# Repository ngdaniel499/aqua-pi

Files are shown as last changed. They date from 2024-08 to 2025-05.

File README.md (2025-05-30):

# AquaPi
Documentation for the Raspberry Pi based water quality monitoring system created by Daniel P. Harrison

## Pi first time setup
### Flash OS
#### Windows
Download Raspberry pi imager https://www.raspberrypi.com/software/

Raspberry Pi Device: Raspberry Pi 1

Operating System: Raspberry PI OS Lite (32-BIT)
	
 	PRETTY_NAME="Raspbian GNU/Linux 12 (bookworm)"
	NAME="Raspbian GNU/Linux"
	VERSION_ID="12"
	VERSION="12 (bookworm)"
	VERSION_CODENAME=bookworm
	ID=raspbian
	ID_LIKE=debian
	HOME_URL="http://www.raspbian.org/"
	SUPPORT_URL="http://www.raspbian.org/RaspbianForums"
	BUG_REPORT_URL="http://www.raspbian.org/RaspbianBugs"
	 
OS Customisation settings: 

	Services>Enable SSH, 

	General>Set username/pw, 

	General>Configure Wireless LAN: add SSID/pin, 

	General>Set Locale settings>Time Zone: Sydney, 

	General>Set Locale settings>Keyboard Layout: US

### RPi setup
  
	sudo apt-get update

	sudo apt-get upgrade

#### configure startup for 1-wire and wlan0
	sudo nano /etc/rc.local
	#!/bin/sh -e
 
	ip link set eth1 down

 	ip link set eth0 down
 
  	ip link set usb0 down
     
	sudo modprobe w1-gpio
	
	sudo modprobe w1-therm

	exit 0
 
#### Turn on 1-wire

Refernce: https://learn.adafruit.com/adafruits-raspberry-pi-lesson-11-ds18b20-temperature-sensing/ds18b20

	sudo raspi-config

		Interfacing Options > 1-Wire > Yes

	sudo reboot

#### Install aqua-pi files and dependencies and setup virtual environment
	sudo apt install git python3 python3-pip -y 
 
 	# if "failed to fetch error / internect connection isn't working delete other connections (nmcli con delete "Wired connection 2")
  
  	cd ~
  
 	git clone https://github.com/ngdaniel499/aqua-pi.git
 
	cd ~/aqua-pi

	python3 -m venv .venv

	source .venv/bin/activate

	pip install -r requirements.txt

#### Configure aquapi

 	cd python-scripts

  	cp Upconfig_template.cfg Upconfig.cfg

 	#edit station name, pump (if required), calibration if data is available. update server IP
  
   	nano Upconfig.cfg 

 	# install cronjob
  
	crontab cronjob.txt

	# edit config if necessary
  
	crontab -e

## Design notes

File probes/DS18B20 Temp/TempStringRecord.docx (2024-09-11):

SIMS SHRP – Sydney Harbour Real Time Monitoring

Daniel Harrison

Dallas DS18B20 Submersible temperature strings record

String ID | Sensor ID (from top) | Position | Nominal Depth | Serial | Cal Correct
001 | 1 | 1m up | | 00000474c314
001 | 2 | Bottom | | 000004756430

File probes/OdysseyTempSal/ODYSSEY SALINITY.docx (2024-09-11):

ODYSSEY SALINITY / TEMP DATA LOGGER

Note that this only covers the trace mode as I have a lot more workto do on other modes of operation.

Trace Mode:

Baud Rate 4800

Parity None

Data Bits 8

Stop Bits 1

Input Buffer Size 32000

1. Software

To wake up the logger send a train of pulses i.e 0x01 01 01 01 01 01 01.

2. Logger

When the logger detects the above pulses it responds with the ascii string

'Hi!' (0x48, 69, 21).

3. Software

The software then confirms logger response and sends String 'T' (0x54)

followed by the ID number of the logger. For the conductivity logger the ID

is 0x1A (Decimal 26).

The software then needs to go into a state waiting for the logger to send

serial data.

4. Logger

Sends values to the software in what appears to be a constant data stream.

The software counts in each byte which is processed and displayed (see raw

data processing below).

If the logger reaches 64 readings it's sends a stop command to the software

(stop command TBD).

Raw Data Processing:

The logger sends data to the software representing the environment it is

monitoring.

This data is processed in such a way as to make the maximum value capable of

being recorded = 65535

Example:

Logger sends 0x09 13.

Binary conversion = 00001001 00010011

Decimal Conversion: MSB = 9 LSB = 19

Software Conversion = MSB + (LSBx256)

i.e. 9 + (19 x 256) = (9 + 4864) = 4873

To exit the trace mode repeat steps 1 & 2 above. The logger will again

respond with the ascii string 'Hi!' (0x48, 69, 21) to confirm it has

stopped.

Hi Daniel,

Yes, we can retrieve the calibration figures if we have the serial numbers.

Engineer

You can get the software to download the data from our website:

http://odysseydatarecording.com/index.php?route=product/category&path=66

The manual is also available:

http://odysseydatarecording.com/index.php?route=information/information&information_id=9

You will also need the calibration files for the units, did they come with

the loggers?

Regards

Richard

Engineer

With reference to the photo supplied:

Green/White = Ground

Blue /White = Transmit (Tx)

Black/White = Recieve (Rx)

Hi Daniel,

Great to hear you are still working on the SHED project. I'm still doing sensor related work but more on the server side infrastructure. Our marine related work (in aquaculture) has stepped up one cost level and we now use embedded Linux and various high cost sensors like Tyco EC250 etc.

Your experience with Odyssey sensors matches exactly with ours. Their tech support is less than helpful. You are right we did reverse engineer the sensor communication. I believe we basically replay communication we captured from the windows software. I do remember thinking is was a bit odd.

Below is a code snippet that may help. This is basically replicating what we saw in our data capture. You should be able to port that across to what ever platform you are using. The last part about sending 256 0x01 bytes is what we saw in the capture. We were never quite sure why it was there! maybe some kind of reset mechanism.

Anyway, hopefully that helps.

Cheers

Chris

//write 0x01 to serial

odyssey_buf[0]=0x01;

i = fos_serial_write(odyssey_serial, odyssey_buf, 1);

if (i != 1) goto fail;

// Brief pause of 0.8 second...

fos_vartimer_sleep(800);

//write 0x54, 0x1a to serial...

odyssey_buf[0]=0x54;

i = fos_serial_write(odyssey_serial, odyssey_buf, 1);

if (i != 1) goto fail;

odyssey_buf[0]=0x1a;

i = fos_serial_write(odyssey_serial, odyssey_buf, 1);

if (i != 1) goto fail;

//next read 4 serial bytes or timeout...

//first erase the odyssey_buffer, flush the serial port ...

for(i=0;i<4;i++)

odyssey_buf[i]=0;

fos_serial_flush (odyssey_serial);

if(fos_serial_timed_read(odyssey_serial,odyssey_buf,4,4)==4)

{

*temperature = (uint16_t)(odyssey_buf[0]) | (((uint16_t)(odyssey_buf[1]))<<8);

*conductivity = (uint16_t)(odyssey_buf[2]) | (((uint16_t)(odyssey_buf[3]))<<8);

success = FOS_TRUE;

} else {

success = FOS_FALSE;

}

//write 0x01 to serial about 256 times...

for(i=0;i<4;i++)

odyssey_buf[i]=0x01;

for(i=0;i<64;i++)

{

fos_serial_write(odyssey_serial, odyssey_buf, 4);

}

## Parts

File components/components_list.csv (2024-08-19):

Item | Description | Cost | Link | Notes
10A PWM Solar Charge Controller 12/24V with USB | - Automatic charge mode selection - Suitable for 12V and 24V battery banks - USB charging port on front panel - Charging Modes: Bulk, Equalise, Float - Supports: Sealed, Gel and Flooded - USB Output: 5V @ 1.2A - Terminals to suit cable up to 4mm2. | $56.95 | https://www.jaycar.com.au/10a-pwm-solar-charge-controller-1224v-with-usb/p/MP3750 | Optional for first experiment
12V 5W Solar Panel with Lead/Clips | 251x205x18mm 5W max power 0.67kg 3m cable | $24.95 | https://www.jaycar.com.au/12v-5w-solar-panel-with-leadclips/p/ZM9050 | Optional for first experiment, could be good to experiment with solar power. Probably need larger solar panel for multiple biopods
Giantz AGM Deep Cycle Battery 12V 25Ah Box Portable Solar Caravan Camping | Overall dimensions: 18 x 7.6 x 16.5 cm Approx. weight: 5.8KG Maximum cycle lIfe: 1400 cycles (@30% DOD) | $ 65 95 | https://www.bigw.com.au/product/giantz-agm-deep-cycle-battery-12v-25ah-box-portable-solar-caravan-camping/p/9900022130 | Should be good enough for first experiment (without solar charging). Might need upgrading for multiple biopods
Linux supported wifi adapter | Wi-Fi 4 802.11n Adapter for PC N150 Nano USB Adapter, 150Mbps, Smallest Wi-Fi 4 Dongle, Win 11 Plug-n-Play, Linux: Ubuntu/Mint Plug-n-Play for Kernel 5.15 and Above, Mac OS, EW-7811Un V2 | 18.09 | https://www.amazon.com/gp/product/B08F2ZNC6J?camp=1789&creative=9325&creativeASIN=B08F2ZNC6J&linkId=80939d577c76fb60d3eb468c10f5b1ba | Driver support for generic wifi adapters might be limited. This one seems to work with Rpi
Telstra Prepaid 4GX Hotspot Black MF985T | It supports speeds up to 600 Mbps. It can support up to 20 devices connected at a time. It has 2 external antenna Ports (antennas not included) for broader coverage. It uses the Telstra 4G network for swift internet access. A 12 month warranty is included. | $149.00 | https://www.officeworks.com.au/shop/officeworks/p/telstra-prepaid-4gx-hotspot-black-mf985t-te210076 | 4G coverage seems sufficient. 4G+5G would be most reliable https://www.telstra.com.au/coverage-networks/our-coverage. Matt might have a better suggestion if he's more familiar with networking
Variable power suppply | - Variable output voltage: 3V DC to 15VDC - Fixed voltage mode: 13.8V DC - Max. output current 40 Amps (continuous) - Ripple & noise: 10m Vrms - Load regulation: 230mV @ 0 - 100% load. - Measures 220(W) x 110(H) x 300(L)mm. - Incredibly light, weighing only 3.5Kgs. - Switchmode | 42.6 | https://www.jaycar.com.au/3v-to-15-volt-dc-40-amp-regulated-switchmode-laboratory-power-supply/p/MP3090 | For testing the system

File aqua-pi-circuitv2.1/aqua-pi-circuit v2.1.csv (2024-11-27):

Id | Designator | Footprint | Quantity | Designation | Supplier and ref
1 | relay control | PinSocket_1x05_P2.54mm_Horizontal | 1 | Conn_01x05_Pin
2 | R1,R4,R3 | R_Axial_DIN0204_L3.6mm_D1.6mm_P5.08mm_Horizontal | 3 | 1k
3 | R2 | R_Axial_DIN0204_L3.6mm_D1.6mm_P5.08mm_Horizontal | 1 | 2k
4 | Chla gain | PinSocket_1x02_P2.54mm_Horizontal | 1 | Conn_01x02_Pin
5 | Sensor in | PinSocket_1x08_P2.54mm_Horizontal | 1 | Conn_01x08_Pin
6 | C2 | C_Disc_D3.0mm_W1.6mm_P2.50mm | 1 | 1uF
7 | J5 | PinSocket_1x02_P2.54mm_Horizontal | 1 | Conn_01x02
8 | RPI | PinHeader_2x20_P2.54mm_Vertical | 1 | Conn_02x20_Odd_Even
9 | Q2,Q1 | TO-92_Inline | 2 | BC549
10 | U1 | PDIP16_300MC_MCH | 1 | MCP3208
11 | C1 | C_Disc_D3.0mm_W1.6mm_P2.50mm | 1 | 100nF

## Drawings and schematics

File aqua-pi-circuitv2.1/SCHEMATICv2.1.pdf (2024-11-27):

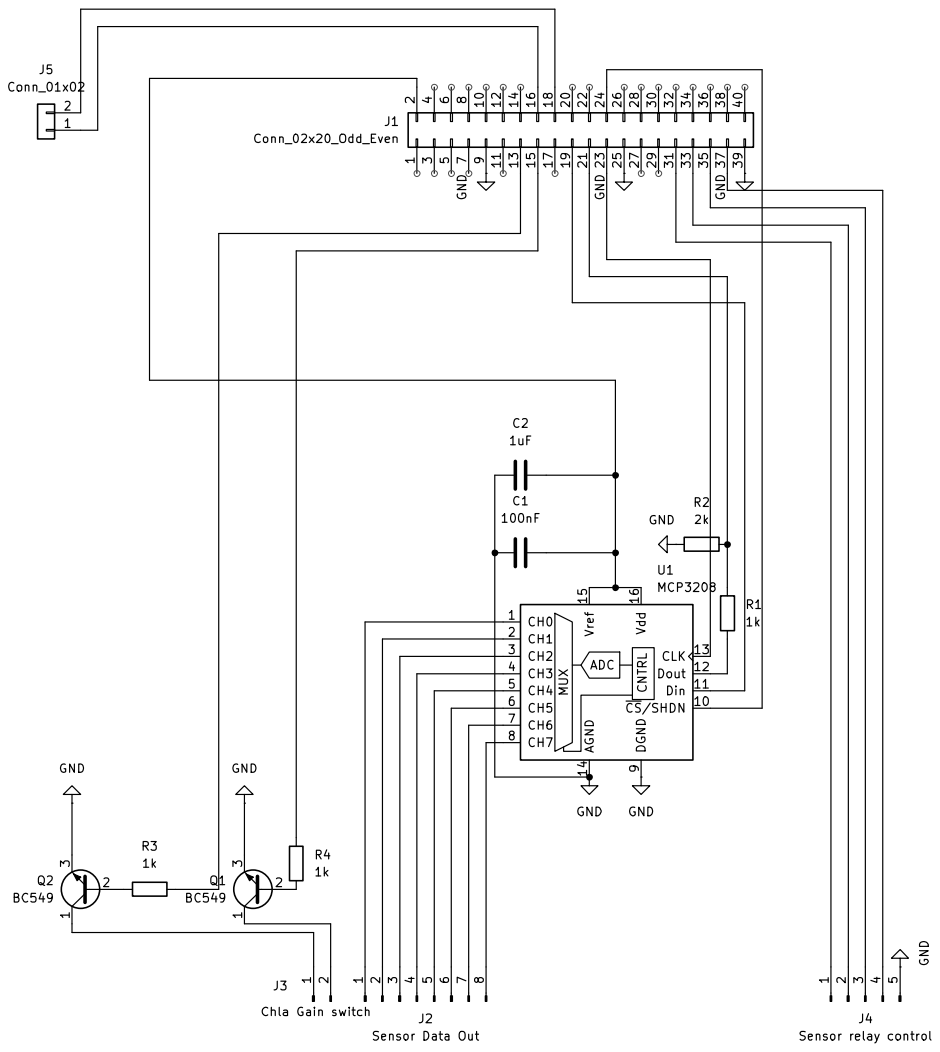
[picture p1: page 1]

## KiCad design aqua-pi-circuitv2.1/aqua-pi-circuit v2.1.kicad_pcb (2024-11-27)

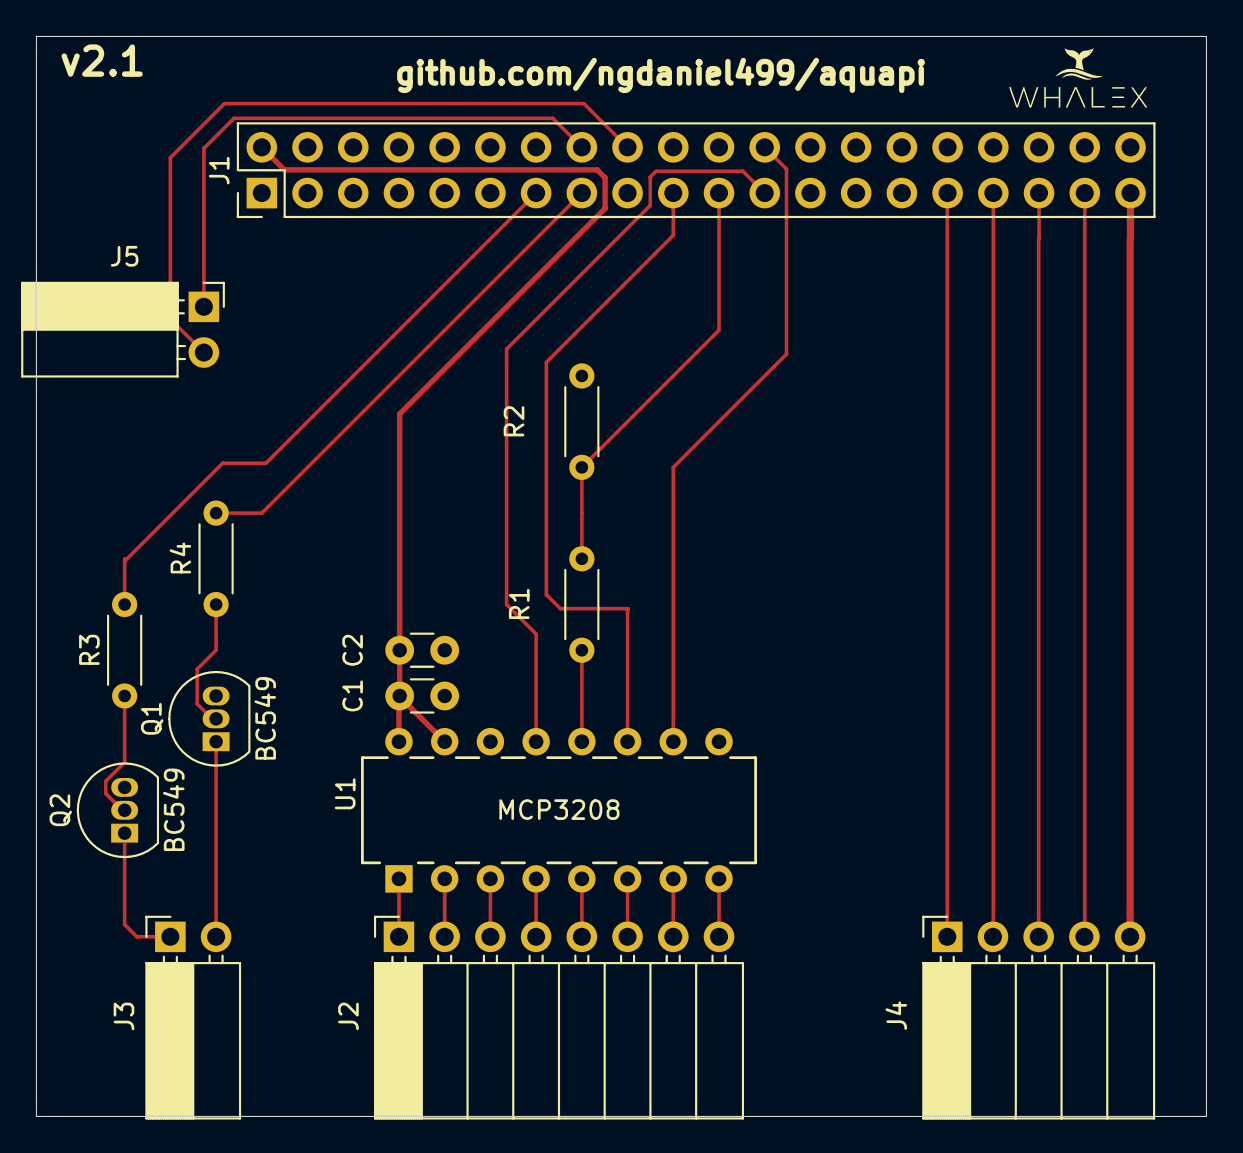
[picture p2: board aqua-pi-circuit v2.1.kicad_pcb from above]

Board: 2 copper layers, 65.0 x 60.0 mm, 14 parts (0 on the bottom side), 27 nets.

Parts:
C1: 100nF; C_Disc_D3.0mm_W1.6mm_P2.50mm
C2: 1uF; C_Disc_D3.0mm_W1.6mm_P2.50mm
J1: Conn_02x20_Odd_Even; PinHeader_2x20_P2.54mm_Vertical
J2: Conn_01x08_Pin; PinSocket_1x08_P2.54mm_Horizontal
J3: Conn_01x02_Pin; PinSocket_1x02_P2.54mm_Horizontal
J4: Conn_01x05_Pin; PinSocket_1x05_P2.54mm_Horizontal
J5: Conn_01x02; PinSocket_1x02_P2.54mm_Horizontal
Q1, Q2: BC549; TO-92_Inline
R1, R3, R4: 1k; R_Axial_DIN0204_L3.6mm_D1.6mm_P5.08mm_Horizontal
R2: 2k; R_Axial_DIN0204_L3.6mm_D1.6mm_P5.08mm_Horizontal
U1: MCP3208; PDIP16_300MC_MCH

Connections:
GND: C1.1, C2.1, J1.9, J1.25, J1.39, J4.5, Q1.3 (E), Q2.3 (E), R2.1, U1.9 (DGND), U1.14 (AGND)
unnamed: C1.2, C2.2, J1.2, U1.15 (Vref), U1.16 (Vdd)
unnamed: J1.13, R3.2
unnamed: J1.15, R4.2
unnamed: J1.16, J5.1
unnamed: J1.18, J5.2
unnamed: J1.19, U1.11 (Din)
unnamed: J1.21, R1.1, R2.2
unnamed: J1.23, U1.13 (CLK)
unnamed: J1.24, U1.10 (~CS/SHDN)
unnamed: J1.31, J4.1
unnamed: J1.33, J4.2
unnamed: J1.35, J4.3
unnamed: J1.37, J4.4
unnamed: J2.1, U1.1 (CH0)
unnamed: J2.2, U1.2 (CH1)
unnamed: J2.3, U1.3 (CH2)
unnamed: J2.4, U1.4 (CH3)
unnamed: J2.5, U1.5 (CH4)
unnamed: J2.6, U1.6 (CH5)
unnamed: J2.7, U1.7 (CH6)
unnamed: J2.8, U1.8 (CH7)
unnamed: J3.1, Q2.1 (C)
unnamed: J3.2, Q1.1 (C)
unnamed: Q1.2 (B), R4.1
unnamed: Q2.2 (B), R3.1
unnamed: R1.2, U1.12 (Dout)

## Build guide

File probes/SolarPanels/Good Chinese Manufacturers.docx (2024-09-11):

Chinese Manufacturers classed as ‘Tier 1 in Australia’ (in my humble opinion)

- Canadian Solar
- CNPV
- CSUN
- Daqo
- ET Solar
- JA Solar
- Jinko Solar
- LDK
- Renesola
- SunTech
- Trina Solar
- Yingli

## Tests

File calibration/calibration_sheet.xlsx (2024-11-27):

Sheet: Sheet1
Serial / material | Blank | AVERAGE RAW READING 400ppb RWT DYE(40ug/L chla equiv) | Calibration curve | Gain setting | Calibration liquid | date
2103415 Titanium | 0 | 838.9090909 | 0.04768097096 | 10x | 400ppb rhodamine WT dye | 2024-10-01
2180450 plastic | 0 | 2020.8 | 0.01979414093 | 10x | 400ppb rhodamine WT dye | 2024-10-01
2180556 plastic | 0 | 2662.5 | 0.01502347418 | 10x | 400ppb rhodamine WT dye | 2024-10-01

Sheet: 2180450
Time | Probe_TempRaw | Probe_TempCal | Condraw | CondCal | SpCond | Salinity | TurbRaw | TurbCal | TurbManu | ChlRaw | ChlVolts | ChlCal | CDOMRaw | CDOMVolts | CDOMCal | CDOMChlEQ | ChlAdj | TempRaw | TempCal
2024-10-17 | Fail | Fail | Fail | Fail | Fail | Fail | Fail | Fail | Fail | 1984 | 1.5984375 | 10.9112 | 0 | 0 | 0 | 0 | 10.9112 | 800 | 6.86
2024-10-17 | Fail | Fail | Fail | Fail | Fail | Fail | Fail | Fail | Fail | 1972 | 1.588769531 | 10.8428 | 0 | 0 | 0 | 0 | 10.8428 | 792 | 6.7752
2024-10-17 | Fail | Fail | Fail | Fail | Fail | Fail | Fail | Fail | Fail | 2064 | 1.662890625 | 11.3672 | 0 | 0 | 0 | 0 | 11.3672 | 793 | 6.7858
2024-10-17 | Fail | Fail | Fail | Fail | Fail | Fail | Fail | Fail | Fail | 2050 | 1.651611328 | 11.2874 | 0 | 0 | 0 | 0 | 11.2874 | 781 | 6.6586
2024-10-17 | Fail | Fail | Fail | Fail | Fail | Fail | Fail | Fail | Fail | 2010 | 1.619384766 | 11.0594 | 0 | 0 | 0 | 0 | 11.0594 | 790 | 6.754
2024-10-17 | Fail | Fail | Fail | Fail | Fail | Fail | Fail | Fail | Fail | 2035 | 1.639526367 | 11.2019 | 0 | 0 | 0 | 0 | 11.2019 | 797 | 6.8282
2024-10-17 | Fail | Fail | Fail | Fail | Fail | Fail | Fail | Fail | Fail | 1998 | 1.609716797 | 10.991 | 0 | 0 | 0 | 0 | 10.991 | 791 | 6.7646
2024-10-17 | Fail | Fail | Fail | Fail | Fail | Fail | Fail | Fail | Fail | 2018 | 1.625830078 | 11.105 | 0 | 0 | 0 | 0 | 11.105 | 783 | 6.6798
2024-10-17 | Fail | Fail | Fail | Fail | Fail | Fail | Fail | Fail | Fail | 2079 | 1.674975586 | 11.4527 | 0 | 0 | 0 | 0 | 11.4527 | 809 | 6.9554
2024-10-17 | Fail | Fail | Fail | Fail | Fail | Fail | Fail | Fail | Fail | 1998 | 1.609716797 | 10.991 | 0 | 0 | 0 | 0 | 10.991 | 790 | 6.754

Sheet: 2180556
Time | Probe_TempRaw | Probe_TempCal | Condraw | CondCal | SpCond | Salinity | TurbRaw | TurbCal | TurbManu | ChlRaw | ChlVolts | ChlCal | CDOMRaw | CDOMVolts | CDOMCal | CDOMChlEQ | ChlAdj | TempRaw | TempCal
2024-10-17 | Fail | Fail | Fail | Fail | Fail | Fail | Fail | Fail | Fail | 2627 | 2.116479492 | 14.5763 | 0 | 0 | 0 | 0 | 14.5763 | 824 | 7.1144
2024-10-17 | Fail | Fail | Fail | Fail | Fail | Fail | Fail | Fail | Fail | 2603 | 2.097143555 | 14.4395 | 0 | 0 | 0 | 0 | 14.4395 | 820 | 7.072
2024-10-17 | Fail | Fail | Fail | Fail | Fail | Fail | Fail | Fail | Fail | 2614 | 2.106005859 | 14.5022 | 0 | 0 | 0 | 0 | 14.5022 | 819 | 7.0614
2024-10-17 | Fail | Fail | Fail | Fail | Fail | Fail | Fail | Fail | Fail | 2695 | 2.171264648 | 14.9639 | 0 | 0 | 0 | 0 | 14.9639 | 816 | 7.0296
2024-10-17 | Fail | Fail | Fail | Fail | Fail | Fail | Fail | Fail | Fail | 2639 | 2.126147461 | 14.6447 | 0 | 0 | 0 | 0 | 14.6447 | 825 | 7.125
2024-10-17 | Fail | Fail | Fail | Fail | Fail | Fail | Fail | Fail | Fail | 2651 | 2.13581543 | 14.7131 | 0 | 0 | 0 | 0 | 14.7131 | 802 | 6.8812
2024-10-17 | Fail | Fail | Fail | Fail | Fail | Fail | Fail | Fail | Fail | 2683 | 2.16159668 | 14.8955 | 0 | 0 | 0 | 0 | 14.8955 | 801 | 6.8706
2024-10-17 | Fail | Fail | Fail | Fail | Fail | Fail | Fail | Fail | Fail | 2721 | 2.192211914 | 15.1121 | 0 | 0 | 0 | 0 | 15.1121 | 797 | 6.8282
2024-10-17 | Fail | Fail | Fail | Fail | Fail | Fail | Fail | Fail | Fail | 2706 | 2.180126953 | 15.0266 | 0 | 0 | 0 | 0 | 15.0266 | 789 | 6.7434
2024-10-17 | Fail | Fail | Fail | Fail | Fail | Fail | Fail | Fail | Fail | 2686 | 2.164013672 | 14.9126 | 0 | 0 | 0 | 0 | 14.9126 | 774 | 6.5844

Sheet: TItanium raw
Time | Probe_TempRaw | Probe_TempCal | Condraw | CondCal | SpCond | Salinity | TurbRaw | TurbCal | TurbManu | ChlRaw | ChlVolts | ChlCal | CDOMRaw | CDOMVolts | CDOMCal | CDOMChlEQ | ChlAdj | TempRaw | TempCal
2024-10-17 | Fail | Fail | Fail | Fail | Fail | Fail | 1534 | 1.235888672 | 8.3462 | 883 | 0.7114013671874999 | 28.45605248 | 0.9713 | 7.374899999999999 | 1409 | 13.3154
2024-10-17 | Fail | Fail | Fail | Fail | Fail | Fail | 1517 | 1.2221923828124999 | 8.2493 | 879 | 0.7081787109 | 28.32714624 | 0.9669000000000001 | 7.2824 | 818 | 7.0508
2024-10-17 | Fail | Fail | Fail | Fail | Fail | Fail | 1528 | 1.231054687 | 8.312 | 851 | 0.6856201171874999 | 27.42480256 | 0.9361 | 7.3759 | 1459 | 13.845400000000001
2024-10-17 | Fail | Fail | Fail | Fail | Fail | Fail | 1517 | 1.2221923828124999 | 8.2493 | 893 | 0.7194580078124999 | 28.778318080000002 | 0.9823000000000001 | 7.2669999999999995 | 822 | 7.0932
2024-10-17 | Fail | Fail | Fail | Fail | Fail | Fail | 1518 | 1.222998047 | 8.254999999999999 | 846 | 0.6815917968749999 | 27.263669760000003 | 0.9306000000000001 | 7.324399999999999 | 1470 | 13.962
2024-10-17 | Fail | Fail | Fail | Fail | Fail | Fail | 1536 | 1.2374999999999998 | 8.3576 | 826 | 0.6654785156249999 | 26.61913856 | 0.9086000000000001 | 7.449 | 824 | 7.114400000000001
2024-10-17 | Fail | Fail | Fail | Fail | Fail | Fail | 1517 | 1.2221923828124999 | 8.2493 | 809 | 0.6517822266 | 26.07128704 | 0.8899 | 7.3594 | 1459 | 13.845400000000001
2024-10-17 | Fail | Fail | Fail | Fail | Fail | Fail | 1491 | 1.201245117 | 8.101099999999999 | 804 | 0.6477539062 | 25.91015424 | 0.8844000000000001 | 7.216699999999999 | 1092 | 9.955200000000001
2024-10-17 | Fail | Fail | Fail | Fail | Fail | Fail | 1542 | 1.2423339843749999 | 8.3918 | 834 | 0.6719238281 | 26.87695104 | 0.9174000000000001 | 7.4744 | 857 | 7.464199999999999
2024-10-17 | Fail | Fail | Fail | Fail | Fail | Fail | 1533 | 1.235083008 | 8.3405 | 793 | 0.6388916015624999 | 25.55566208 | 0.8723000000000001 | 7.4682 | 1302 | 12.1812
2024-10-17 | Fail | Fail | Fail | Fail | Fail | Fail | 1561 | 1.2576416015624998 | 8.5001 | 810 | 0.6525878906 | 26.1035136 | 0.891 | 7.6091 | 1048 | 9.488800000000001
2024-10-17 | Fail | Fail | Fail | Fail | Fail | Fail | 4095 | 3.299194336 | 22.9439 | 61 | 0.049145507812499996 | 1.96582016 | 0.0671 | 22.8768 | 1223 | 11.343800000000002
2024-10-17 | Fail | Fail | Fail | Fail | Fail | Fail | 4095 | 3.299194336 | 22.9439 | 82 | 0.06606445312 | 2.64257792 | 0.0902 | 22.8537 | 1201 | 11.110600000000002
 |  |  |  |  |  |  |  |  |  | 838.9090909

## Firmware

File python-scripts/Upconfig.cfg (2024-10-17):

[Section1]
# 1wire temp string settings
base_dir=/sys/bus/w1/devices/
slave_dir=/w1_slave
# General Settings
data_dir=data/
stationid=AQUAPI3test
readinterval=15
cdompin = 19
chlpin = 26
condpin = 13
turbpin = 6
temppin = 24
pumppin = 23
#pumprun is true/false
pumprun = true
pumptime = 15
cdomadc = 1
chladc = 0
turbadc = 2
tempadc = 3


# Calibration Settings
conda=0.00000002
condb=-0.0003
condc=9.7027
condd=-14489
Probe_tempslope = 1
Probe_tempint = 1
#tempslope=0.0106
#tempint=-1.62
tempslope = 1
tempint = 1
chlslope=0.0057
chlint=-0.3976
cdomslope=0.03222656
cdomint=0
cdomchlslope=0.0011
cdomchlint=0
turbslope=0
turbint=0

#new HTTPS server
server_url=http://13.210.60.50/upload

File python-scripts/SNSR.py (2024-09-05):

import os
import glob
import time
import datetime

import sys
import serial

import traceback

import spidev
import wiringpi2 as wiringpi
import RPi.GPIO as GPIO
from decimal import*
import signal

THREEPLACES = Decimal(10) ** -3
THREEPLACES=10**-3
GPIO.setwarnings(False)
GPIO.setmode(GPIO.BCM)

SPICLK=11
SPIMISO=9
SPIMOSI=10
SPICS=8



GPIO.setup(SPIMOSI,GPIO.OUT)
GPIO.setup(SPIMISO,GPIO.IN)
GPIO.setup(SPICLK, GPIO.OUT)
GPIO.setup(SPICS,  GPIO.OUT)


# function  to get data from specified pin of ADC
def readadc(adcnum, clockpin, mosipin, misopin, cspin):
    if ((adcnum > 7) or (adcnum <0)):
        return -1

    GPIO.output(cspin,True)
    GPIO.output(clockpin,False)
    GPIO.output(cspin,False)

    commandout=adcnum
    commandout|=0x18
    commandout<<=3
    for i in range(5):
        if (commandout & 0x80):
            GPIO.output(mosipin,True)
        else:
            GPIO.output(mosipin,False)
        commandout<<=1
        GPIO.output(clockpin,True)
        GPIO.output(clockpin,False)

    adcout=0
    for i in range(14):
        GPIO.output(clockpin,True)
        GPIO.output(clockpin,False)
        adcout<<=1
        if(GPIO.input(misopin)):
            adcout|=0x1
    GPIO.output(cspin,True)

    adcout>>=1
    return adcout

def readchl(chlpin, chladc,chlslope, chlint):
    try:
        
        #Turn on chl probe using relay
        wiringpi.pinMode(chlpin, 1)
        wiringpi.digitalWrite(chlpin, 0)
        time.sleep(5)
        #read data from ADC chip
        #read data from ADC Chl 0
        ADC_Chl=chladc
        resp=readadc(ADC_Chl,SPICLK,SPIMOSI,SPIMISO,SPICS)
        # Format response from ADC chip
        ChlRaw = resp
        ChlVolts = (float(ChlRaw) / 4096) * 3.3
        ChlCal = (ChlRaw * chlslope) + chlint 
        print("ChlRaw is:", ChlRaw)
        print("ChlVolts is:", ChlVolts)
        print("ChlCal is:", ChlCal)
        #turn off probe
        wiringpi.digitalWrite(chlpin, 1)
        return ChlRaw, ChlVolts, ChlCal
    except:
        print('Read Chl Fail')
        ChlRaw = 'Fail'
        ChlVolts = 'Fail'
        ChlCal = 'Fail'
        wiringpi.digitalWrite(chlpin, 1)
        return ChlRaw, ChlVolts, ChlCal
    
def readcdom(cdompin, cdomadc,cdomslope, cdomint, cdomchlslope, cdomchlint):
    try:
        #Turn on CDOM probe using relay 
        wiringpi.pinMode(cdompin, 1)
        wiringpi.digitalWrite(cdompin, 0)
        time.sleep(5)
        #read data from ADC chip    
        #read data from ADC Chl 1
        ADC_Chl=cdomadc
        resp=readadc(ADC_Chl,SPICLK,SPIMOSI,SPIMISO,SPICS)
        # Format response from ADC chip
        CDOMRaw = resp
        CDOMVolts = (float(CDOMRaw) / 4096) * 3.3
        CDOMCal = (CDOMRaw * cdomslope) + cdomint
        CDOMChlEQ = (CDOMRaw * cdomchlslope) + cdomchlint
        print("CDOMRaw is:", CDOMRaw)
        print("CDOMVolts is:", CDOMVolts)
        print("CDOMCal is:", CDOMCal)
        print("CDOM Chl EQ is:", CDOMChlEQ)
        #turn off probe
        wiringpi.digitalWrite(cdompin, 1)
        return CDOMRaw, CDOMVolts, CDOMCal, CDOMChlEQ
    except:
        #print 'Read CDOM Fail'
        CDOMRaw = 'Fail'
        CDOMVolts = 'Fail'
        CDOMCal = 'Fail'
        CDOMChlEQ = 'Fail'
        wiringpi.digitalWrite(cdompin, 1)
        return CDOMRaw, CDOMVolts, CDOMCal, CDOMChlEQ

def readtemp(temppin, tempadc,tempslope, tempint):
    try:
        
        #Turn on chl probe using relay
        wiringpi.pinMode(temppin, 1)
        wiringpi.digitalWrite(temppin, 1)
        time.sleep(5)
        #read data from ADC chip
        #read data from ADC Chl 2
        ADC_Chl=tempadc
        resp=readadc(ADC_Chl,SPICLK,SPIMOSI,SPIMISO,SPICS)
        # Format response from ADC chip
        TempRaw = resp
        TempVolts = (float(TempRaw) / 4096) * 3.3
        TempCal = (TempRaw * tempslope) + tempint 
        print("TempRaw is:", TempRaw)
        print("TempVolts is:", TempVolts)
        print( "TempCal is:", TempCal)
        #turn off probe
        wiringpi.digitalWrite(temppin, 0)
        return TempRaw, TempVolts, TempCal
    except:
        print( 'Read Temp Fail')
        TempRaw = 'Fail'
        TempVolts = 'Fail'
        TempCal = 'Fail'
        wiringpi.digitalWrite(temppin, 0)
        return TempRaw, TempVolts, TempCal
    
def readturb(turbID, turbslope, turbint):
    try:
#    for x in range(0,1):
    #Set up serial comms. Sensor connected by Prolific USB to Serial Converter     
        port = serial.Serial("/dev/ttyUSB1", baudrate=1200, bytesize=7, parity='E', stopbits=1, xonxoff=0, rtscts=0, timeout=5)
        #Clear buffers
        port.flushInput()
        port.flushOutput()
        #Send command to initiate measurement
        port.write('single\r')
        time.sleep(1)
        #Read data
        response= port.readlines()
        #print(response)
        #Clear buffers and read again
        port.flushInput()
        port.flushOutput()
        #Send command to initiate measurement
        port.write('single\r')
        time.sleep(1)
        response= port.readlines()        
        #print(response)
        respvalues = []
        for t in response[3].split():
            try:
                respvalues.append(float(t))
            except ValueError:
                pass    
        TurbManu = respvalues[0]
        TurbRaw = respvalues[1]
        TurbCal = (TurbRaw*turbslope)+turbint
        print( "TurbManu value is:", TurbManu)
        print( "TurbCal value is:", TurbCal)
        print( "TurbRaw is:", TurbRaw)
        return TurbRaw, TurbCal, TurbManu
    except:
        print( 'ReadTurbFail')
        TurbRaw = 'Fail'
        TurbCal = 'Fail'
        TurbManu = 'Fail'
        return TurbRaw, TurbCal, TurbManu
def readcond(condpin, condID, conda, condb, condc, condd, tempslope, tempint):
    try:
        wiringpi.pinMode(condpin, 1)
        wiringpi.digitalWrite(condpin, 0)
        time.sleep(5)
        #Set up serial comms. Sensor connected by Prolific USB to Serial Conveter 
        port = serial.Serial("/dev/ttyUSB0", baudrate=4800, bytesize=8, parity='N', stopbits=1, xonxoff=0, rtscts=0, timeout=10)
        
        # wake up odyssey sensor
        response = "No"
        trycount = 0
        while response != "Hi!":
            port.flushInput()
            port.flushOutput()
            port.write(chr(0x01))
            response=port.read(3)
            print(response)
            if trycount == 3 :
                break
            trycount = trycount + 1
        
        #Start trace mode by sending "T" followed by sensor ID
        time.sleep(1)
        port.flushOutput()
        port.flushInput()
        port.write(chr(0x54))
        port.write(chr(0x1a))   

        #Read data, data delivered in stream of 4 bytes representing 2 lots of 0-65535 values for temperature / salinity
        data=port.read(4)
        
        #Test Code used to check calculations
        #data1 =chr(int("0x09",16))
        #data2 =chr(int("13",16))
    
        #Calculate Temp & Conductivity
        TempRaw = ord(data[0])+ord(data[1])*256
        CondRaw = ord(data[2])+ord(data[3])*256
        # Perform Calibrations
        TempCal = (TempRaw*tempslope) + tempint
        CondCal = (CondRaw**3)*conda + (CondRaw**2)*condb + CondRaw*condc + condd    
        #Calculate SpCond and Salinity
        SpCond = CondCal/(1+0.0191*(TempCal-25))
        R = SpCond/53087
        k1 = 0.0120
        k2 = -0.2174
        k3 = 25.3283
        k4 = 13.7714
        k5 = -6.4778
        k6 = 2.5842
        Salinity = k1 +(k2*R**(1/2))+(k3*R)+(k4*R**(3/2))+(k5*R**2)+(k6*R**(5/2))
        #End trace mode
        response = "No"
        while response !="Hi!":
            port.flushInput()
            port.flushOutput()
            for count in range(0, 256):
                port.write(chr(0x01))
            response=port.read(3)
        wiringpi.digitalWrite(condpin, 1)    
        return TempRaw, CondRaw, TempCal, CondCal, SpCond, Salinity
    except:
        #print 'Read Temp/Cond Fail'
        TempRaw = 'Fail'
        CondRaw = 'Fail'
        TempCal = 'Fail'
        CondCal = 'Fail'
        SpCond = 'Fail'
        Salinity = 'Fail'
        wiringpi.digitalWrite(condpin, 1)
        return TempRaw, CondRaw, TempCal, CondCal, SpCond, Salinity

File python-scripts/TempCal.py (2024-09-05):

#!/usr/bin/python
#----------------------------------------------------------------------------------------------#
# NAME:         AquaPi.py
# CREATED:      August 10 2014
# CREATED BY:   Daniel P Harrison, University of Sydney 
# 	        	Some intital code adapted from Bjorn Veltman & Adafruit
# Modification 1 By: Shariq Riaz, University of Sydney
#                       ADC read script is changed and pin numbers
# FUNCTION:     Operates the AquaPi Sensor Suite created by Daniel P Harrison as part of the Sydney
#               Harbour Research Program - Real Time Monitoring
#
# run this script as: sudo python AquaPi.py config.cfg
# parameters values are given in Upconfig.cfg
#----------------------------------------------------------------------------------------------
import os
import glob
import time
import datetime
import ConfigParser
import sys
import serial
#from ftplib import FTP
import traceback
#from ftpupallAuto import ftpupload
import spidev
import wiringpi2 as wiringpi
import RPi.GPIO as GPIO
from decimal import*
import signal

from SNSR import readadc,readchl,readcdom,readturb,readcond

wiringpi.wiringPiSetupGpio()

"""THREEPLACES = Decimal(10) ** -3
THREEPLACES=10**-3
GPIO.setwarnings(False)
GPIO.setmode(GPIO.BCM)

SPICLK=11
SPIMISO=9
SPIMOSI=10
SPICS=8
SENSOR1=22
SENSOR2=27
RELAY=17

GPIO.setup(SPIMOSI,GPIO.OUT)
GPIO.setup(SPIMISO,GPIO.IN)
GPIO.setup(SPICLK, GPIO.OUT)
GPIO.setup(SPICS,  GPIO.OUT)
GPIO.setup(SENSOR1,  GPIO.OUT)
GPIO.setup(SENSOR2,  GPIO.OUT)
GPIO.setup(RELAY,  GPIO.OUT)
"""

        
def open_outputfile(fpath, stationid):
    outfile = 'TempCal-' + stationid + '_' + time.strftime("%Y_%m_%d_%H")+'H.csv'
    fpathf = os.path.join(fpath,outfile)
    if os.path.exists(fpathf):
        f = open(fpathf,'a')
    else:
        f = open(fpathf,'w')
        headerline = 'Time,Tempraw,TempCal,Condraw,CondCal,SpCond,Salinity,Turbraw,TurbCal,TurbManu,ChlRaw,ChlVolts,ChlCal,CDOMRaw,CDOMVolts,CDOMCal'
        f.write(str(headerline))
        f.write('\n')
    return f, outfile, fpathf

# Start Main Program Here
try:
    config = ConfigParser.ConfigParser()
    configfilewithpath =  '/home/pi/PythonScripts/FINAL_CODE/Upconfig.cfg'
    config.read(configfilewithpath)
    config_file = configfilewithpath.split('\\')[-1]
    base_dir = config.get('Section1', 'base_dir')
    slave_dir = config.get('Section1', 'slave_dir')
    fpath = config.get('Section1', 'fpath')
    stationid = config.get('Section1', 'stationid')
    readinterval = config.getfloat('Section1', 'readinterval')
    cdompin = config.getint('Section1', 'cdompin')
    chlpin = config.getint('Section1', 'chlpin')    
    pumppin = config.getint('Section1', 'pumppin')
    pumpflush = config.getint('Section1', 'pumpflush')
    server_ip = config.get('Section1', 'server_ip')
    username = config.get('Section1', 'username')
    password = config.get('Section1', 'password')
    ftp_dir = config.get('Section1', 'ftp_dir')
    #Get calibration constants
    chlslope = config.getfloat('Section1', 'chlslope')
    chlint = config.getfloat('Section1', 'chlint')
    cdomslope = config.getfloat('Section1', 'cdomslope')
    cdomint = config.getfloat('Section1', 'cdomint')
    turbslope = config.getfloat('Section1', 'turbslope')
    turbint = config.getfloat('Section1', 'turbint')
    conda = config.getfloat('Section1', 'conda')
    condb = config.getfloat('Section1', 'condb')
    condc = config.getfloat('Section1', 'condc')
    condd = config.getfloat('Section1', 'condd')
    tempslope = config.getfloat('Section1', 'tempslope')
    tempint = config.getfloat('Section1', 'tempint')    
    #create output file
    f, outfile, fpathf = open_outputfile(fpath, stationid)
    #create variable for current file hour 
    now = datetime.datetime.now()
    checkhour = now.hour
    
    #    for x in range(0, 10):

    # Flush flow chamber
    wiringpi.wiringPiSetupGpio()
    wiringpi.pinMode(pumppin, 1)
    wiringpi.digitalWrite(pumppin, 1)
#   time.sleep(1*60)

    for x in range (0,100):

        # Conduct Measurements

        # Temperature / conductivity
        TempRaw, CondRaw, TempCal, CondCal, SpCond, Salinity = readcond('USB0',conda,condb,condc, condd, tempslope, tempint)


        #time.sleep(5)
        # For testing print results to screen
        print('Tempraw',TempRaw)
        print('Condraw',CondRaw)
        print('TempCal',TempCal)
        print('CondCal',CondCal)
        print('SpCond',SpCond)
        print('Salinity',Salinity)
	sys.stdout.flush()

        # Write results to file
        r = '%s,%s,%s,%s,%s,%s,%s' % (time.strftime("%d-%m-%Y %H:%M:%S"), TempRaw, TempCal, CondRaw, CondCal, SpCond, Salinity)
        f.write(str(r))
        f.write('\n')
    f.close
    # Stop Pump
    wiringpi.digitalWrite(pumppin, 0)
    
except:
    tb = sys.exc_info()[2]
    tbinfo = traceback.format_tb(tb)[0]
    error_msg = tbinfo + " " + str(sys.exc_info()[1])
    print error_msg
    f.write(error_msg)
    f.close()

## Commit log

2024-08-19 added components list draft
    [components list.csv]
2024-08-19 update components list
    [components list.csv, components list.csv.xlsx]
2024-08-19 renamed files
    [components list.csv.xlsx, components_list.csv]
2024-09-05 Old OS deprecated. cant install build dependencies / kernel headers. Updated to run on Raspberry Pi OS lite (Raspbian GNU / Linux 12 (bookworm)) Updated code to work with python3 Added pip requiremen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
2024-09-05 renamed from final.py to main.py properly, added data folder
    [SPIT_2024_09_05_14H.csv]
2024-09-05 renamed FINAL_CODE to python-scripts
    [SPIT_2024_09_05_14H.csv, SPIT_2024_09_05_15H.csv]
2024-09-13 changed upload data to account for newest file updating
    [SPIT_2024_09_05_14H.csv, SPIT_2024_09_05_15H.csv]
2024-09-13 added exception case for dead server
2024-09-25 renamed scripts in prep for pump script
2024-09-25 untested pump code
2024-09-25 working pump and cron script for pump
2024-09-25 removed deprecated pump setup / ftup from main.py
2024-09-25 Update README.md. fixed .venv and added new crontab line to run pump at 15mins offset by 7m
2024-11-06 added calibration sheet (calibrated against 400ppb RWT at 10x gain)
    [calibration_sheet.xlsx]
2024-11-26 added revamped aquapi circuit files
    [aqua-pi-circuit v2.1-B_Cu.gbr, aqua-pi-circuit v2.1-B_Mask.gbr, aqua-pi-circuit v2.1-B_Paste.gbr, aqua-pi-circuit v2.1-B_Silkscreen.gbr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]
2024-12-28 added archived function to separate current and old files
